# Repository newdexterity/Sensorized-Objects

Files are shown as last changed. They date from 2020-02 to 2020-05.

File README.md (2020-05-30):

# Sensorized-Objects

# ReadMe Contents
- Folder Contents
- Introduction
- Object Assembly
- Fabrication
- How to Place Polhemus Sensors and Retro-Reflective Markers in Objects
- IMU Object Setup

# Folder Contents
In this repository you can find:
* CAD and STL files of the rigid and soft manipulation objects. 
* Code examples for processing data.
* In-hand manipulation example data with the T42 and NDX-A* robot hands. 

# Introduction
The human hand is Nature's most versatile and dexterous end-effector and it has been a source of inspiration for roboticists for over 50 years. Recently, significant industrial and research effort has been put into the development of dexterous robot hands and grippers. Such end-effectors offer robust grasping and dexterous, in-hand manipulation capabilities that increase the efficiency, precision, and adaptability of the overall robotic platform. This work focuses on the development of modular, sensorized objects that can facilitate benchmarking of the dexterity and performance of hands and grippers. The proposed objects aim to offer; a minimal, sufficiently diverse solution, efficient pose tracking, and accessibility. The object manufacturing instructions, 3D models, and assembly information are made publicly available through the creation of a corresponding repository.

<p align="center">
  
</p>

# Object Assembly
explodedView3
Each object of the sensorized object set consists of 5 to 13 parts:
* a plastic screw (which holds the object together)
* two object halves (these halves can be objects of any size and surface stiffness)
* two removable urethane marker mounts
* eight removable object weights (optional components)

# Fabrication 

## 3D printing
STL files are included in the CAD folder.
### Plastic Threads
If the plastic screw does not screw into the object, a **M8 tap and die** can be used to fix any tolerancing errors introdruced by the 3D printing proccess.

[comment]: <> (add image of plastic screw and object being tapped)
tapping5sec (https://www.youtube.com/watch?v=iwGn_2lOhc0&feature=youtu.be "tapping5sec")

**NOTE:** The plastic screws should not be overtightened or they will break (using SLA or SLS printing proccesses can increase the strength of the screw).

## Molding
### Urethane/ Silicone Mixing
**Note:** Before molding the mold should be sprayed with mold release and **ensure not to spray objects** as this may prevent the objects soft skin from sticking correctly to the soft object halves. 
1. Read the urethane/ silicone instructions to determine **mix ratio** and **work time**
    - Work time will determine how quickly you will need to degas and inject the material into the mold.
2. Pour appropriate resin and hardener portions as instructed by the suppliers mix ratio.
3. Mix together thoroughly.
5. Place mixture into vacuum chamber to degas. 
6. Pour or inject urethane/ silicone mixture into mold. 
### Markers
Instructional videos for molding the markers can be found below. When molding the markers using a softer urethane or silicon (e.g **Smooth On Vytaflex 30**) will make insertion and removal of the markers into and out of the object halves significantly easier.
#### Optical Markers/ Polhemus Markers
flatMaker (https://www.youtube.com/watch?v=eXIwOtoV1qc "flatMaker")
#### ArUco Marker Mounts
ARMaker (https://www.youtube.com/watch?v=xcrOEh82KFU "ARMaker")

### Soft Objects 
Before molding the objects a narrow nozzle syringe needs to be prepared in order for the chosen urethane or silicone to reach the small narrow spaces in the mold without air bubbles.

Materials needed to prepare long nozzle syringe: 
* Syringe
* Heat shrink
* Pliers 
* Super glue

The materials can be seen depicted below with an accompanying video demonstrating how to fabricate one.

<p align="center">
  
</p>

syringe5sec (https://www.youtube.com/watch?v=B0mpWGTTy3A&feature=youtu.be "syringe5sec")

#### Mold Assembly and Preparation
Assembly of the molds can be seen below with exploded views of the mold and assembly videos. 

Cube and radially split cylinder molds will require aluminum tape to the mold seams to prevent potential leaking. 

Components required for molds: 
* For object halves with internal threads
    - 1 x M8 screw of 20mm length
* For object halves without threads
    - 1x M8 screw of 35mm length
    - 1 x M8 nut

##### Cube Mold

<p align="center">
  
</p>

CubeMoldPreparations (https://www.youtube.com/watch?v=x2nqksHXXIw "CubeMoldPreparations")

**Note:** The walls of the mold should be parallel to the soft object core as shown in the image below to prevent misalignment. 
<p align="center">
  
</p>

##### Cylinder Mold
* Radially Split Cylinder

<p align="center">
  
</p>

CylinderMoldPreparations (https://www.youtube.com/watch?v=_m07TIoGHqI "CylinderMoldPreparations")

* Axially Split Cylinder

<p align="center">
  
</p>

##### Sphere Mold

<p align="center">
  
</p>

#### Molding Process
moldingObject (https://www.youtube.com/watch?v=eo5qOiTZaQk "moldingObject")

## Demolding

### Markers
#### Optical Markers/ Polhemus Markers

OpticalMarkers (https://www.youtube.com/watch?v=Dwkm1ft7N5k "OpticalMarkers")

For Polhemus markers only the first 2 steps of the video need to be followed. The last step is only relevant if you require optical markers.

#### ArUco Marker Mounts

ARMarkers (https://www.youtube.com/watch?v=l4PmQHS5-48 "ARMarkers")

### Soft Objects 
The demolding proccess of cubes and radially split cylinders are the same, as well as for the spheres and axially split cylinders. 

CylinderDemold (https://www.youtube.com/watch?v=J1zPYWYStN0&feature=youtu.be "CylinderDemold")

ShpereDemold (https://www.youtube.com/watch?v=wvo3y9mB7Rw&feature=youtu.be "ShpereDemold")

# How to Place Polhemus Sensors and Retro-Reflective Markers in Objects
## Retro-Reflective Markers
For  retro-reflective markers only the first 9 seconds of the below video need to be watched. 
1. Assemble object.
2. Insert retro-reflective markers into marker cavities. 
## Polhemus Micro Sensors
1. Insert micro sensor through the hole of the Polhemus urethane marker. 
2. Insert the micro sensor into the 2mm hole at the base of the screw. 
    **Note:** If the sensor can't fit into hole a 2mm drill bit will need to be used to correct the dimensions of the hole. 
3. Place blu tack around the cable at the base of the screw. This will prevent the sensor from falling out, but will still allow it to be pulled out if a sigincant tug force on the cable is experienced. 
4. Once the screw and the sensor are in place, the Polhemus urethane marker can then be inserted into the corresponding object half.

Polhemus (https://www.youtube.com/watch?v=4mxdQY6hf8g&feature=youtu.be "Polhemus")

# IMU Object SetUp
## IMU Schematic 
The Object will contain:
- 1x Arduino Nano IOT (consists of onboard IMU and bluetooth comunication)
- 1x Powerboost 500 (a boost converter board for 5V output)
- 1x 180mah lipo battery
arduinoSetup
## Installation of IMU
Denpending on the chosen object the length of the soldered wires will vary. For small objects only the rigid cube and cylinder shapes are supported. The imu implementation is suppoerted accross all medium and large sized objects support.

The small and medium ranges, plus the large sphere have the electronics installed in one of the 2 object halves. For the large objects (cube and cylinder) the ellectronics are supported in 1 of the 8 object weights. The relevant CAD files can be found above under the CAD Folder.

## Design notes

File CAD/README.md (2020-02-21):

# Sensorized-Objects CAD Files
In this folder you can find the CAD files and needed to manufacture the components in the object set. 

## ReadMe Contents
- Folder Contents
- Object Assembly
- Fabrication
- How to Place Polhemus Sensors and Retro-Reflective Markers in Objects

## Folder Contents
The objects have been organised into there relative sizes and the rigid and soft surface components are present in all sizes. 
**Large size -** Contains the lagest sized object set CAD files <br/>
**Medium size -** Contains the medium sized object set CAD files <br/>
**Small size -** Contains the smallest sized object set CAD files <br/>
**Common parts -** Contains  CAD files common components across the 3 sizes (e.g. markers) <br/>

# Object Assembly
explodedView3
Each object of the sensorized object set consists of 5 to 13 parts:
* a plastic screw (which holds the object together)
* two object halves (these halves can be objects of any size and surface stiffness)
* two removable urethane marker mounts
* eight removable object weights (optional components)

# Fabrication 

## 3D printing
STL files are included in the CAD folder.
### Plastic Threads
If the plastic screw does not screw into the object, a **M8 tap and die** can be used to fix any tolerancing errors introdruced by the 3D printing proccess.

[comment]: <> (add image of plastic screw and object being tapped)
tapping5sec (https://www.youtube.com/watch?v=iwGn_2lOhc0&feature=youtu.be "tapping5sec")

**NOTE:** The plastic screws should not be overtightened or they will break (using SLA or SLS printing proccesses can increase the strength of the screw).

## Molding
### Urethane/ Silicone Mixing
**Note:** Before molding the mold should be sprayed with mold release and **ensure not to spray objects** as this may prevent the objects soft skin from sticking correctly to the soft object halves. 
1. Read the urethane/ silicone instructions to determine **mix ratio** and **work time**
    - Work time will determine how quickly you will need to degas and inject the material into the mold.
2. Pour appropriate resin and hardener portions as instructed by the suppliers mix ratio.
3. Mix together thoroughly.
5. Place mixture into vacuum chamber to degas. 
6. Pour or inject urethane/ silicone mixture into mold. 
### Markers
Instructional videos for molding the markers can be found below. When molding the markers using a softer urethane or silicon (e.g **Smooth On Vytaflex 30**) will make insertion and removal of the markers into and out of the object halves significantly easier.
#### Optical Markers/ Polhemus Markers
flatMaker (https://www.youtube.com/watch?v=eXIwOtoV1qc "flatMaker")
#### ArUco Marker Mounts
ARMaker (https://www.youtube.com/watch?v=xcrOEh82KFU "ARMaker")

### Soft Objects 
Before molding the objects a narrow nozzle syringe needs to be prepared in order for the chosen urethane or silicone to reach the small narrow spaces in the mold without air bubbles.

Materials needed to prepare long nozzle syringe: 
* Syringe
* Heat shrink
* Pliers 
* Super glue

The materials can be seen depicted below with an accompanying video demonstrating how to fabricate one.

<p align="center">
  
</p>

syringe5sec (https://www.youtube.com/watch?v=B0mpWGTTy3A&feature=youtu.be "syringe5sec")

#### Mold Assembly and Preparation
Assembly of the molds can be seen below with exploded views of the mold and assembly videos. 

Cube and radially split cylinder molds will require aluminum tape to the mold seams to prevent potential leaking. 

Components required for molds: 
* For object halves with internal threads
    - 1 x M8 screw of 20mm length
* For object halves without threads
    - 1x M8 screw of 35mm length
    - 1 x M8 nut

##### Cube Mold

<p align="center">
  
</p>

CubeMoldPreparations (https://www.youtube.com/watch?v=x2nqksHXXIw "CubeMoldPreparations")

**Note:** The walls of the mold should be parallel to the soft object core as shown in the image below to prevent misalignment. 
<p align="center">
  
</p>

##### Cylinder Mold
* Radially Split Cylinder

<p align="center">
  
</p>

CylinderMoldPreparations (https://www.youtube.com/watch?v=_m07TIoGHqI "CylinderMoldPreparations")

* Axially Split Cylinder

<p align="center">
  
</p>

##### Sphere Mold

<p align="center">
  
</p>

#### Molding Process
moldingObject (https://www.youtube.com/watch?v=eo5qOiTZaQk "moldingObject")

## Demolding

### Markers
#### Optical Markers/ Polhemus Markers

OpticalMarkers (https://www.youtube.com/watch?v=Dwkm1ft7N5k "OpticalMarkers")

For Polhemus markers only the first 2 steps of the video need to be followed. The last step is only relevant if you require optical markers.

#### ArUco Marker Mounts

ARMarkers (https://www.youtube.com/watch?v=l4PmQHS5-48 "ARMarkers")

### Soft Objects 
The demolding proccess of cubes and radially split cylinders are the same, as well as for the spheres and axially split cylinders. 

CylinderDemold (https://www.youtube.com/watch?v=J1zPYWYStN0&feature=youtu.be "CylinderDemold")

ShpereDemold (https://www.youtube.com/watch?v=wvo3y9mB7Rw&feature=youtu.be "ShpereDemold")

# How to Place Polhemus Sensors and Retro-Reflective Markers in Objects
## Retro-Reflective Markers
For  retro-reflective markers only the first 9 seconds of the below video need to be watched. 
1. Assemble object.
2. Insert retro-reflective markers into marker cavities. 
## Polhemus Micro Sensors
1. Insert micro sensor through the hole of the Polhemus urethane marker. 
2. Insert the micro sensor into the 2mm hole at the base of the screw. 
    **Note:** If the sensor can't fit into hole a 2mm drill bit will need to be used to correct the dimensions of the hole. 
3. Place blu tack around the cable at the base of the screw. This will prevent the sensor from falling out, but will still allow it to be pulled out if a sigincant tug force on the cable is experienced. 
4. Once the screw and the sensor are in place, the Polhemus urethane marker can then be inserted into the corresponding object half.

Polhemus (https://www.youtube.com/watch?v=4mxdQY6hf8g&feature=youtu.be "Polhemus")

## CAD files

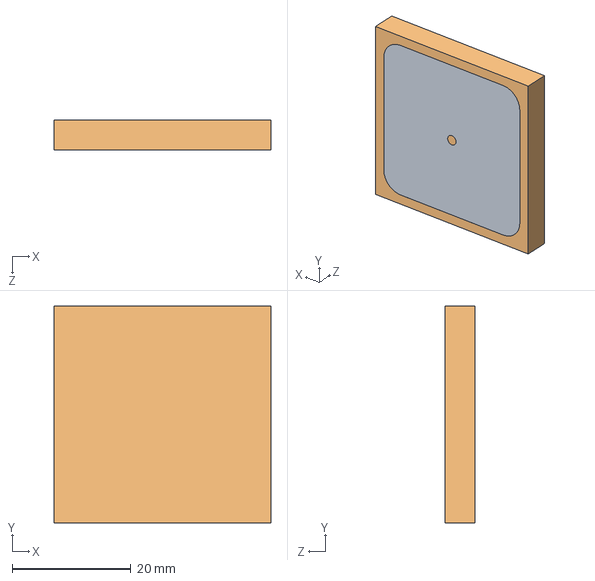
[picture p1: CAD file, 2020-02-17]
CAD/common parts/PolhemusMarkerMould.SLDASM
36.5 x 36.5 x 5.00 mm
PolhemusMarker
PolhemusMarkerMould

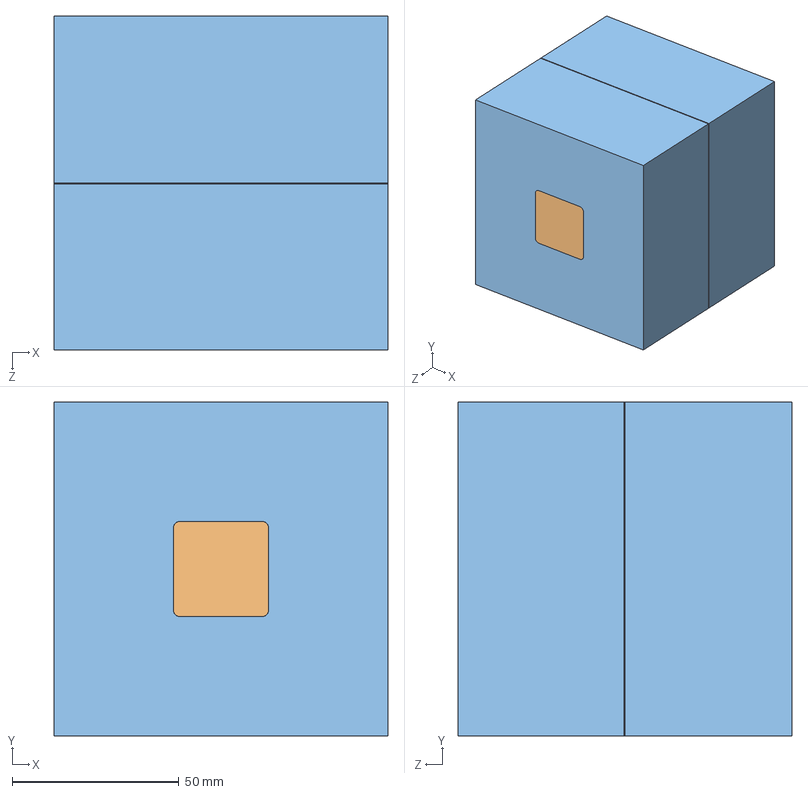
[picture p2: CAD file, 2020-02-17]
CAD/Large size/Rigid_Objects/Cube/largeRigidCubeAssem.SLDASM
100.0 x 100.0 x 100.0 mm
large_rigid_cube_screw_half1
markerCav x 2
large_rigid_cube_screw_half2

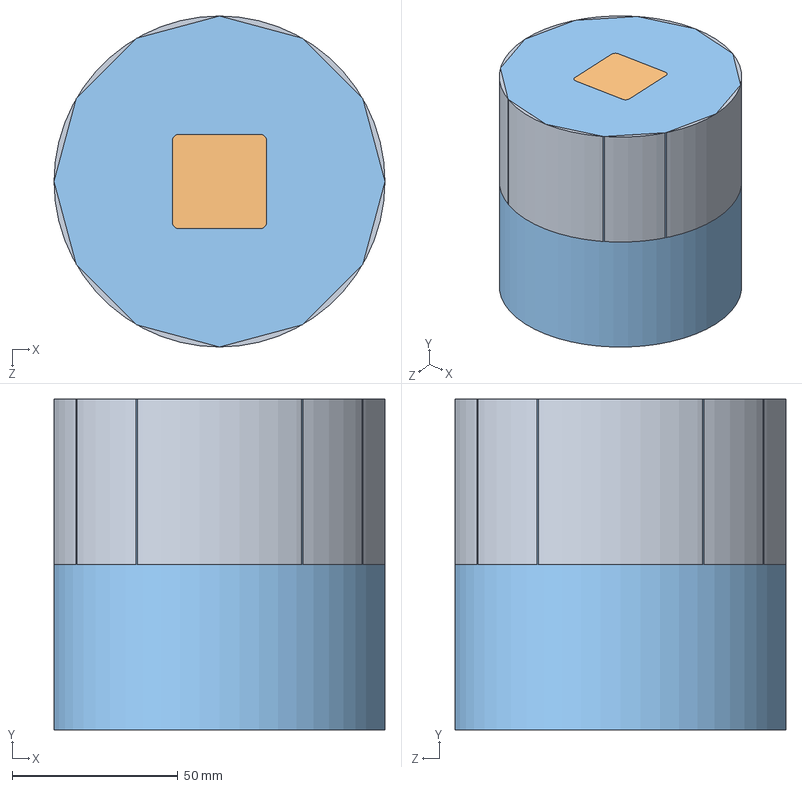
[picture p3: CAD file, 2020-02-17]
CAD/Large size/Rigid_Objects/Cylinder/largeRigidCylinderAssem.SLDASM
100.0 x 100.0 x 100.0 mm
largeRigidCylinder_screw_half_1
markerCav x 2
largeRigidCylinder_screw_half_2

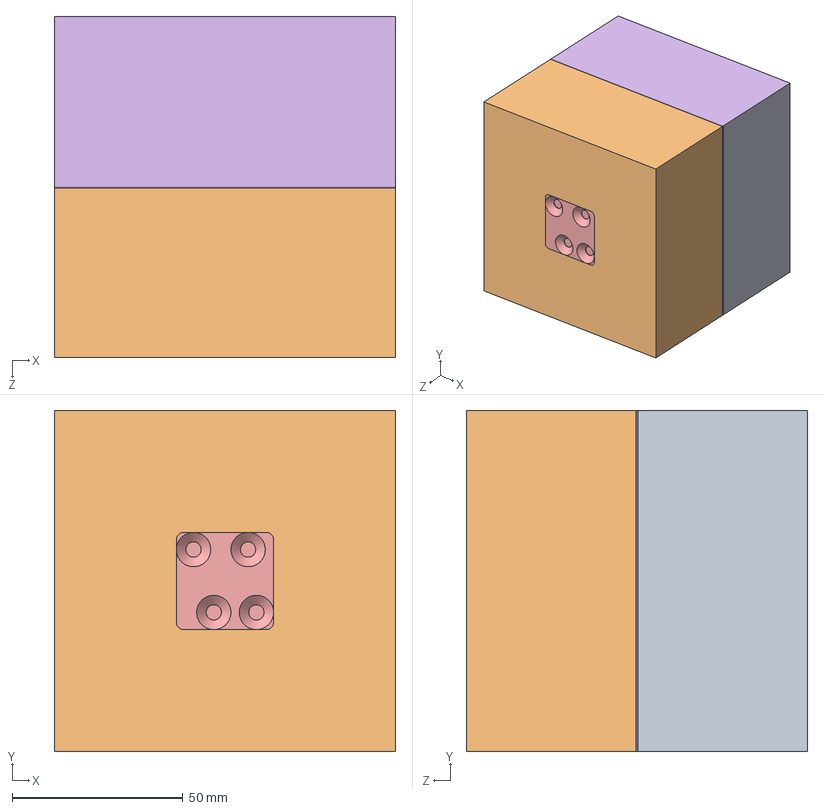
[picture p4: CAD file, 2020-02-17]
CAD/Large size/Soft_Objects/Cube/exp_large_soft_assem.SLDASM
100.0 x 100.0 x 100.0 mm
large_soft_cube_screw_half1
large_soft_cube_screw_half2
largecubeWieght x 8
largeScrew
marker x 2
largeSoftCubeSkin x 2

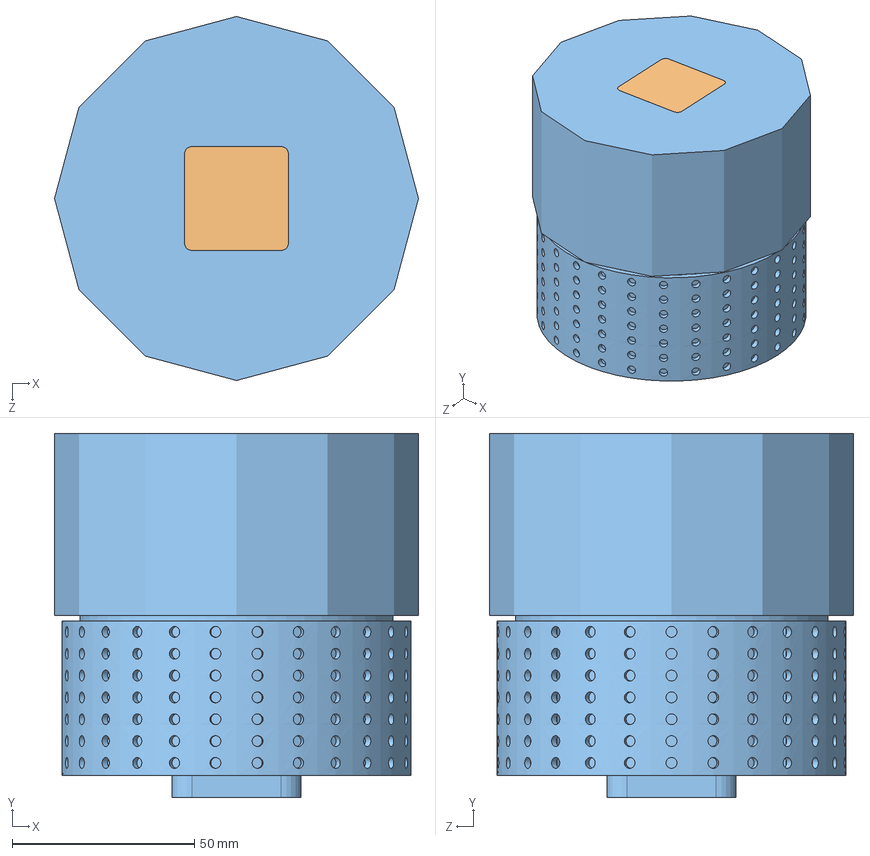
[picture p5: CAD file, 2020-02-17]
CAD/Large size/Soft_Objects/Cylinder/largeSoftCylinderAssem.SLDASM
100.0 x 100.0 x 100.0 mm
large_soft_rigidCylinder_screw_half_1
markerCav x 2
large_soft_rigidCylinder_screw_half_2

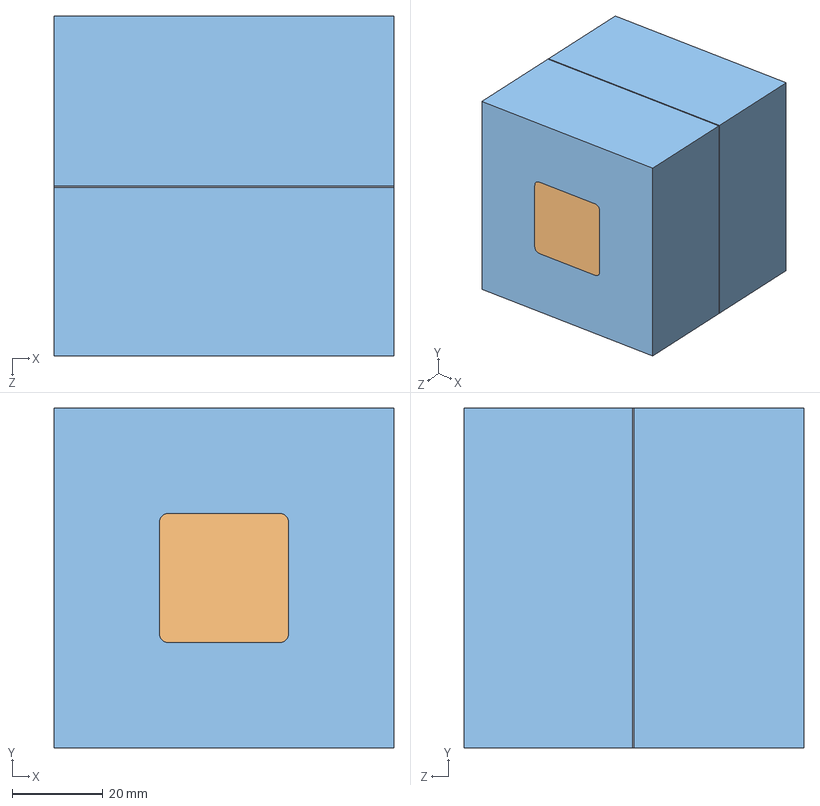
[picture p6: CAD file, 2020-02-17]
CAD/Medium size/Rigid_Objects/Cube/medRigidCubeAssem.SLDASM
75.0 x 75.0 x 75.0 mm
med_rigid_cube_screw_half1
markerCav x 2
med_rigid_cube_screw_half2

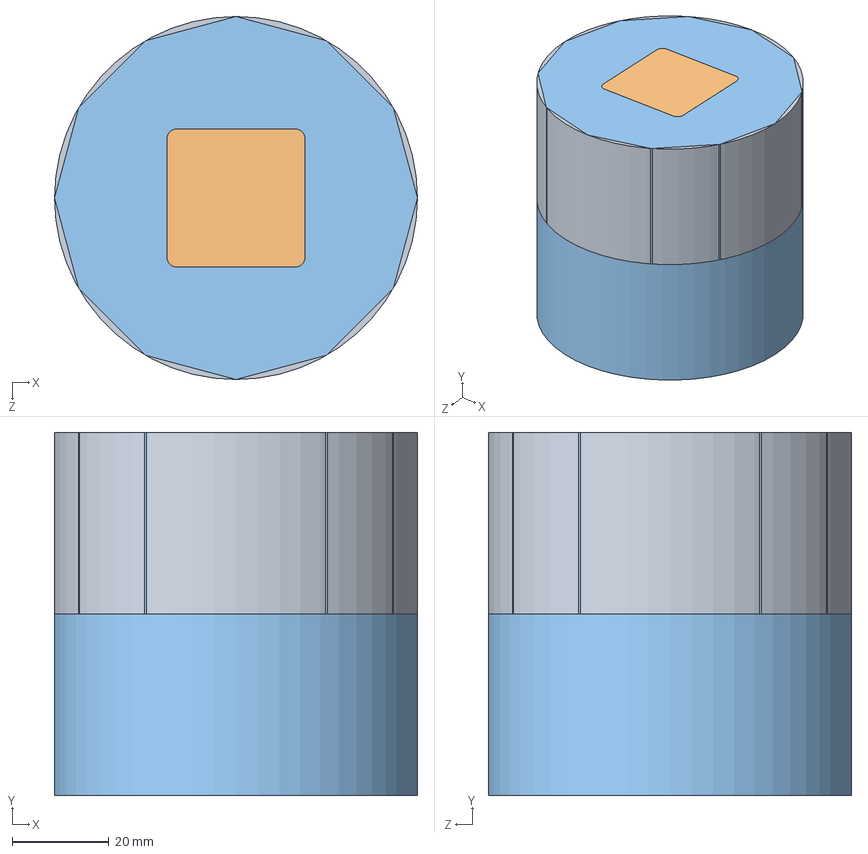
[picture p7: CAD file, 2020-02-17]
CAD/Medium size/Rigid_Objects/Cylinder/mediumRigidCylinderAssem.SLDASM
75.0 x 75.0 x 75.0 mm
mediumRigidCylinder_screw_half_1
markerCav x 2
mediumRigidCylinder_screw_half_2

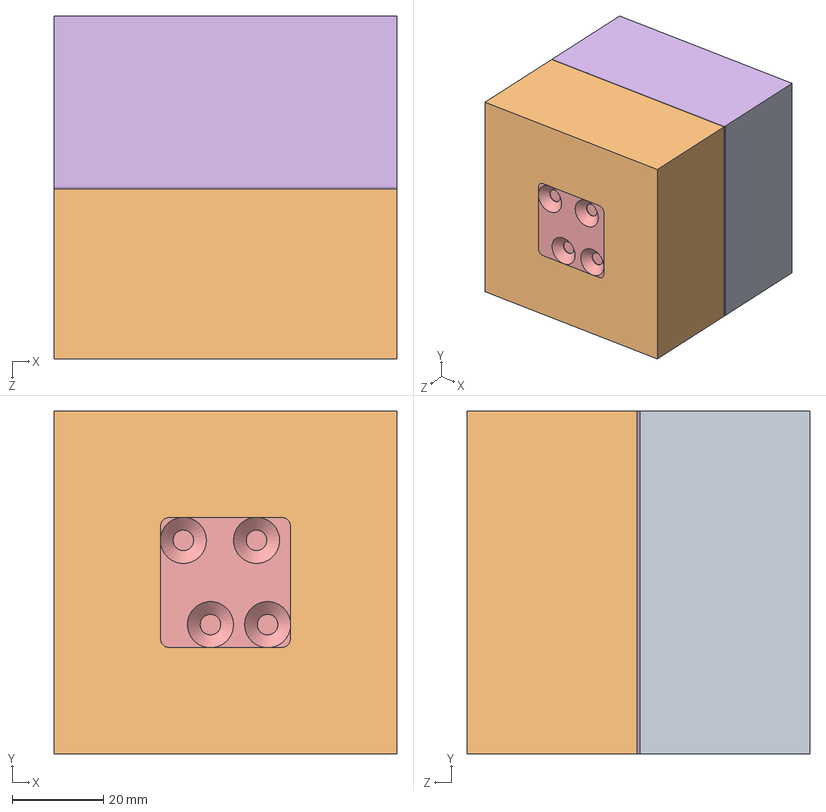
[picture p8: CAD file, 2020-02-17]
CAD/Medium size/Soft_Objects/Cube/exp_medium_cube_assem.SLDASM
75.0 x 75.0 x 75.0 mm
med_soft_cube_screw_half1
med_soft_cube_screw_half2
mediumCubeWieght x 8
mediumScrew
marker x 2
mediumcubeSkin x 2

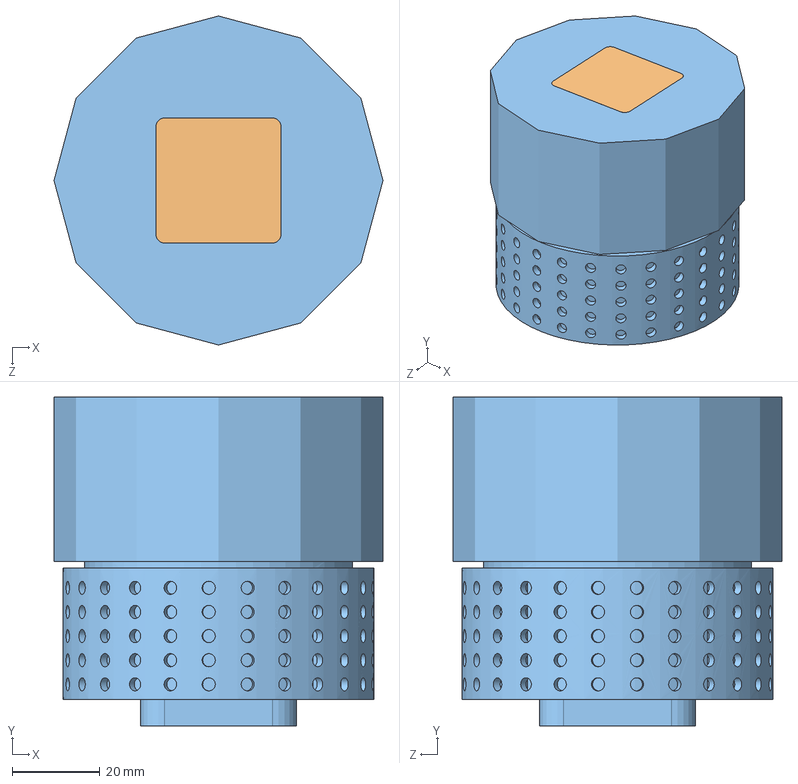
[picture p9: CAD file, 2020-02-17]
CAD/Medium size/Soft_Objects/Cylinder/mediumSoftCylinderAssem.SLDASM
75.0 x 75.0 x 75.0 mm
med_soft_cylinder_screw_half_1
markerCav x 2
med_soft_cylinder_screw_half_2

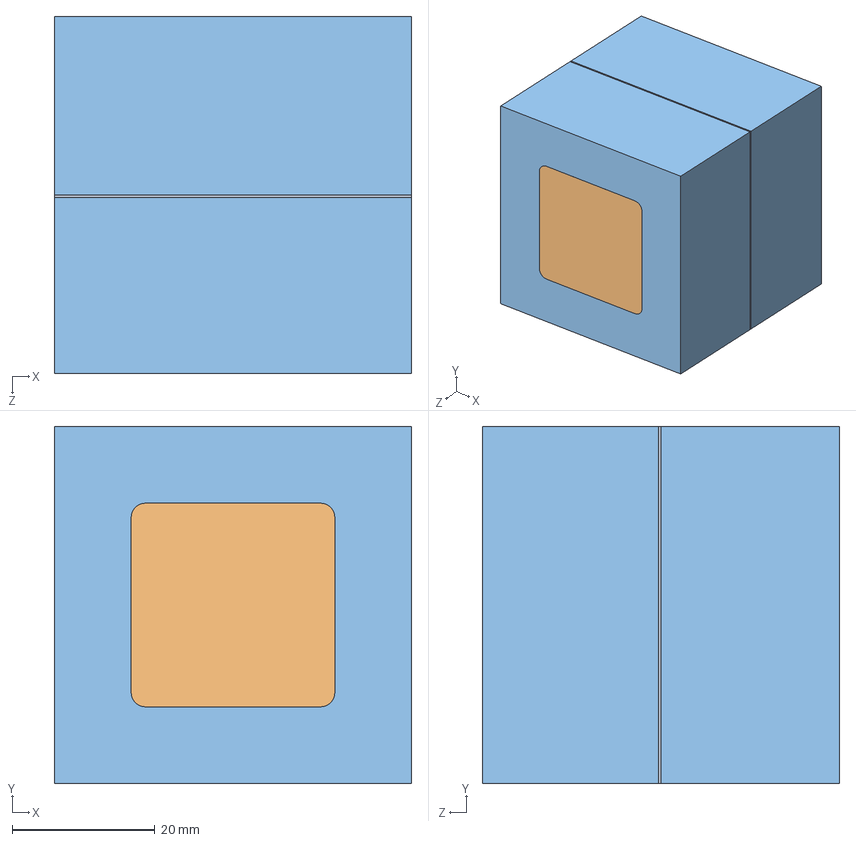
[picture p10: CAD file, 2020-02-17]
CAD/Small size/Rigid_Objects/Cube/smallRigidCubeAssem.SLDASM
50.0 x 50.0 x 50.0 mm
smallRigidCube_screw_half1
markerCav x 2
smallRigidCube_screw_half2

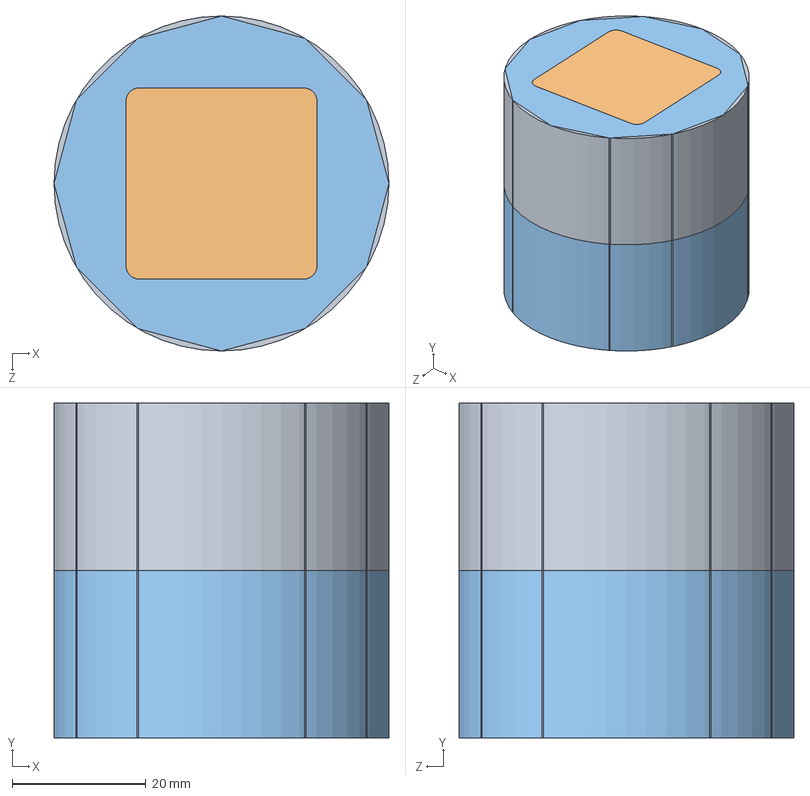
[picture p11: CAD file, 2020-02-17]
CAD/Small size/Rigid_Objects/Cylinder/smallRigidCylinderAssem.SLDASM
50.0 x 50.0 x 50.0 mm
smallRigidCylinder_screw_half_1
markerCav x 2
smallRigidCylinder_screw_half_2

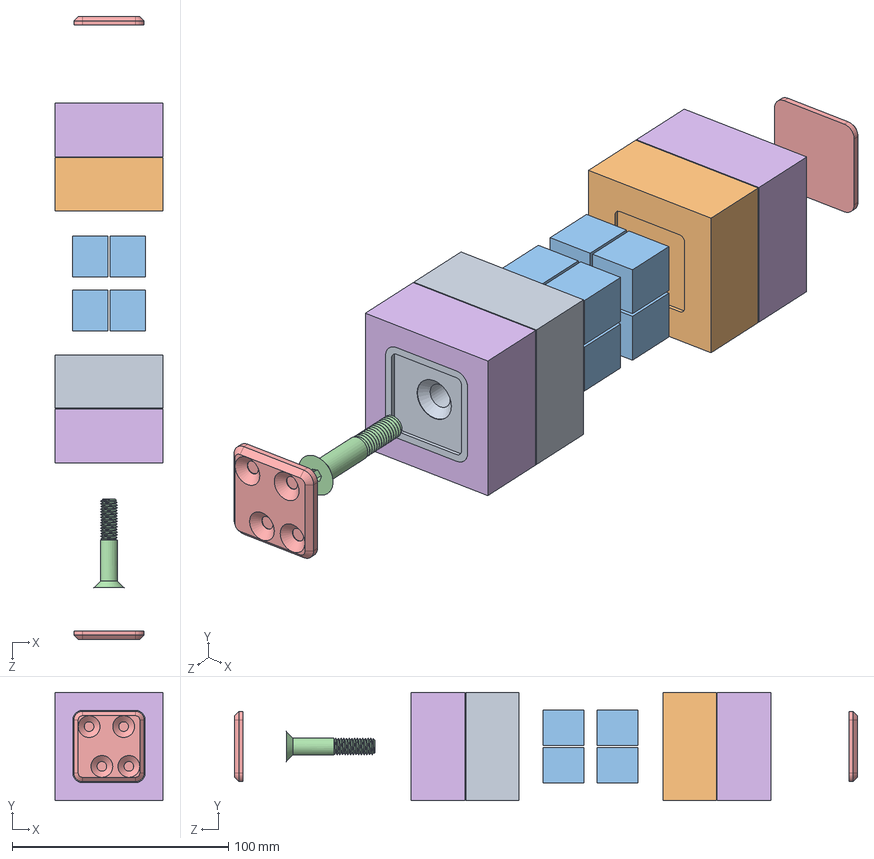
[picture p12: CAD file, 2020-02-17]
CAD/Small size/Soft_Objects/Cube/exp_soft_cube_assem.SLDASM
50.0 x 50.0 x 288.4 mm
small_soft_cube_screw_half1
small_soft_cube_screw_half2
small_cube_wieght x 8
screw
marker x 2
small_soft_cubeSkin x 2

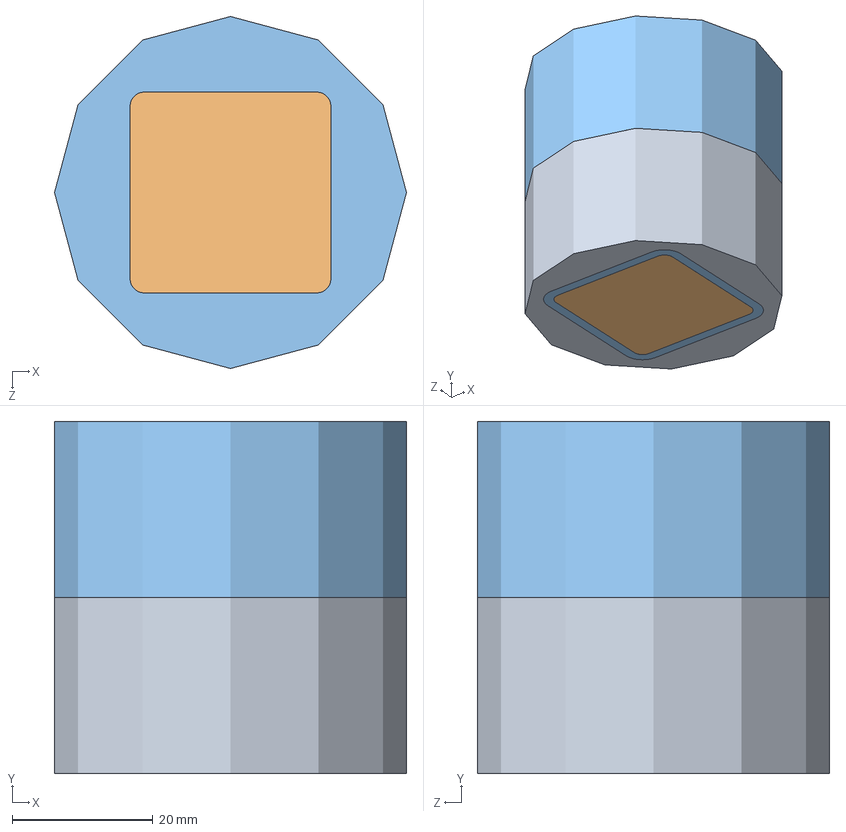
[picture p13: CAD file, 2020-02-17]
CAD/Small size/Soft_Objects/Cylinder/small_soft_cylinder_assem.SLDASM
50.0 x 50.0 x 50.0 mm
small_soft_cylinder_screw_half_1
markerCav x 2
small_soft_cylinder_screw_half_2

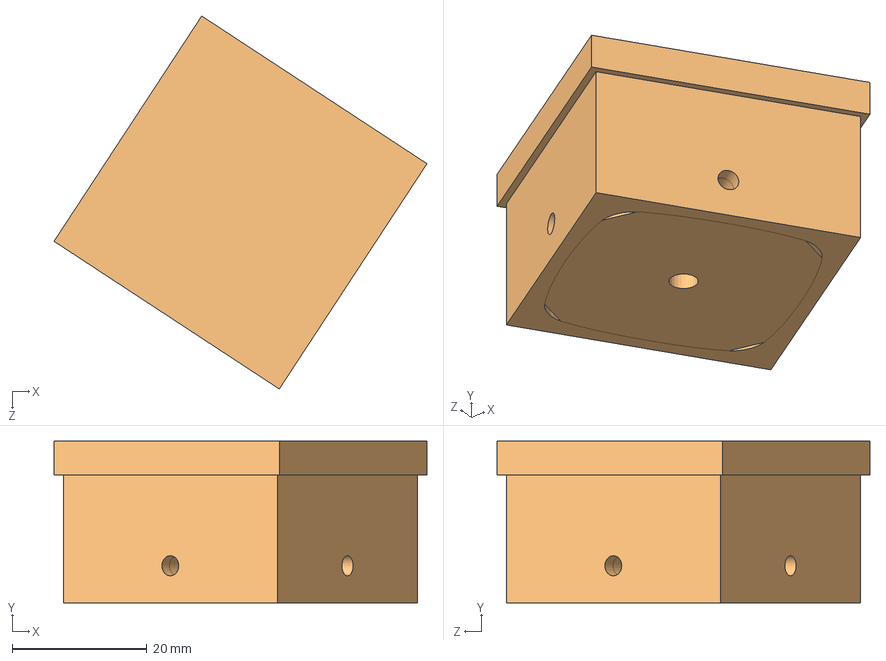
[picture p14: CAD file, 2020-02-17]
CAD/common parts/arSphereMarkerMouldAssem.SLDASM
55.4 x 24.0 x 55.4 mm

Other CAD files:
CAD/Large size/Soft_Objects/Cube/largeSoftCubeAssem.SLDASM
CAD/Small size/Soft_Objects/Cube/small_soft_cubeAssem.SLDASM
CAD/common parts/ARMarkerMould.SLDASM
CAD/common parts/markerMould.SLDASM
CAD/Large size/Rigid_Objects/Cube/large_rigid_cube_screw_half1.SLDPRT
CAD/Large size/Rigid_Objects/Cube/large_rigid_cube_screw_half2.SLDPRT
CAD/Large size/Rigid_Objects/Cylinder/Common/ARMarkerMould.STL
CAD/Large size/Rigid_Objects/Cylinder/Common/PolhemusMarkerMould.STL
CAD/Large size/Rigid_Objects/Cylinder/largeRigidCylinder_screw_half_1.SLDPRT
CAD/Large size/Rigid_Objects/Cylinder/largeRigidCylinder_screw_half_2.SLDPRT
CAD/Large size/Rigid_Objects/Cylinder/largeRigidVertCylinder_half_1.SLDPRT
CAD/Large size/Rigid_Objects/Cylinder/largeRigidVertCylinder_half_2.SLDPRT
CAD/Large size/Rigid_Objects/Sphere/large_rigid_sphereHalf1.SLDPRT
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

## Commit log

2019-08-16 Uploading all the current files
    This upload contains the new objects (rigid and soft) with there respective molds. In addition to this code examples, manipulation data, protocols, and benchmarks are also included.
    [Assem2.SLDASM, NDX_A_rigid_cube_pitch_1.csv, NDX_A_rigid_cube_power_GR_1.csv, NDX_A_rigid_cube_precision_GR_1.csv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]
2019-11-18 New size objects
    New object sizes: small, medium and large have now been added for both soft and rigid objects
    [Assem2.SLDASM, cubeAssem.SLDASM, cubeBase.SLDPRT, cubeBase.STL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]
2019-11-19 AR/polhemus markers added
    new markers
    [ARMarkerMould.SLDASM, ARMarkerMould.SLDPRT, ARMarkerMould.STL, ARMarkerMount.SLDPRT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]
2020-02-14 moulds
    addition of aruco marker moulds
    [ARMarkerMould.STL, AR_Cylinder_marker.SLDPRT, AR_Sphere_marker.SLDPRT, PolhemusMarkerMould.STL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]
2020-05-30 IMU based objects
    [cube_screw_half1_IMU.SLDPRT, large soft_sphereHalf1_IMU.STL, large_rigid_sphereHalf1_IMU.SLDPRT, large_rigid_sphereHalf1_IMU.STL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]
2020-05-30 Revert "IMU based objects"
    This reverts commit 2b44704d62884f936c147bb8cd1335c6f0cceadc.
    [cube_screw_half1_IMU.SLDPRT, large soft_sphereHalf1_IMU.STL, large_rigid_sphereHalf1_IMU.SLDPRT, large_rigid_sphereHalf1_IMU.STL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]
2020-05-30 Revert "Revert "IMU based objects""
    This reverts commit f5904857dfecf76f785f5b504ea1f8a60df6f8fb.
    [cube_screw_half1_IMU.SLDPRT, large soft_sphereHalf1_IMU.STL, large_rigid_sphereHalf1_IMU.SLDPRT, large_rigid_sphereHalf1_IMU.STL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]
